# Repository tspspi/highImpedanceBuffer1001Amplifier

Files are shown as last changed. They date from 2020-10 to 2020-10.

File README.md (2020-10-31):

# Simple combined buffer and 1001x amplifier

This is a simple circuit that combines two OpAmps with 1 GHz
bandwidth to form a buffer amplifier followed by an 1001 times
amplifying amplifier.

This circuit has been designed to measure the beam profile of
an low current electron beam. The shunt has been designed as wire
resistor to be easily adaptable. The OpAmps have been selected
with up to 1 GHz bandwidth to allow for measurement of deflection
frequency inside an modulated beam.

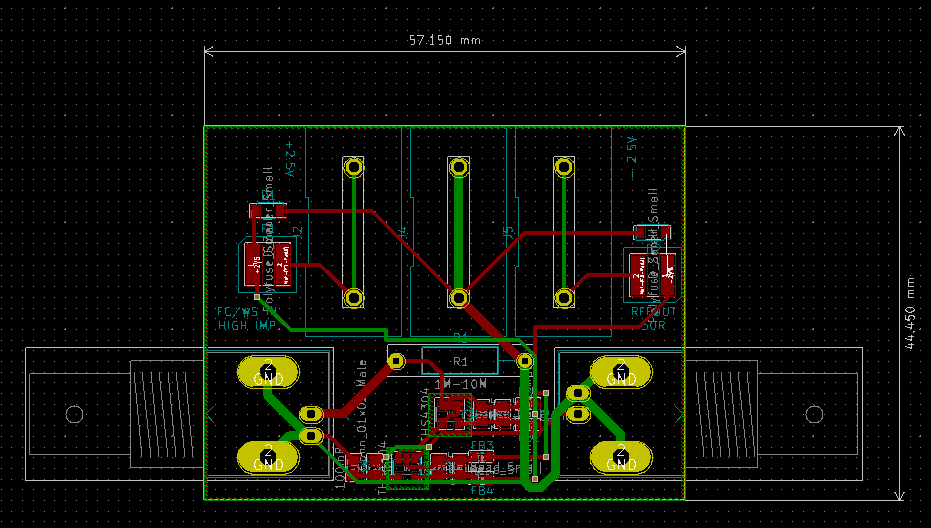
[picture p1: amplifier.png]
PCB layout


Schematic

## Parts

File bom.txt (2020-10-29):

#	FarnellNo	Title																								Unit price		Price
2	1076296		BNC Connector																				 2.920				 5.840
1	2519856		100 R +- 0.1%, 100 mW																 0.883				 0.883
1	2328114		100 mR																							 0.114				 1.114
2	3117744		THS4304																							 6.030				12.060
2	1759412		3.3 uF																							 0.165				 0.825
2	1740665		0.1 uF																							 0.0953				 0.953
4	3282195		Ferrite Beds																				 0.026			   0.104
1 	1698986		Banenstecker Buchse 4mm, grün												 1.89					 1.89
1 	1698983		Banenstecker Buchse 4mm, schwarz										 1.89					 1.89
1 	1698982		Banenstecker Buchse 4mm, rot												 1.89					 1.89
2	2285354		Zener-Diode, 3 V, 1 W, SOD-123F											 0.0832				0.1664
2 	1822219		Rückstellbare Sicherung, PPTC, 2016 (550 mA)				 0.9520				1.9040

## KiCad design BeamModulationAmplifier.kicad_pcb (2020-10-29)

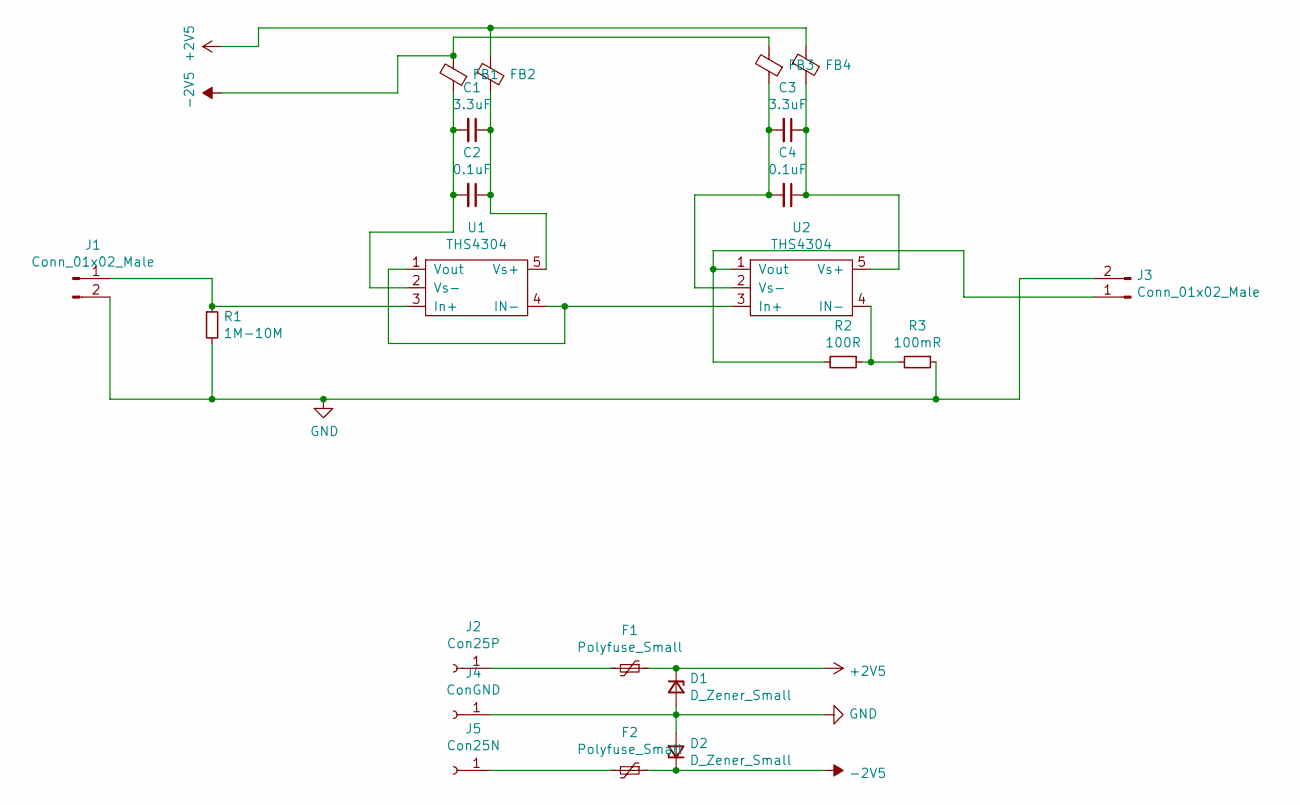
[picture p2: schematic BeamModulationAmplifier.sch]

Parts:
C1, C3: 3.3uF; R_0805_2012Metric
C2, C4: 0.1uF; R_0805_2012Metric
D1, D2: D_Zener_Small; Mini2
F1, F2: Polyfuse_Small; Generic2016
FB1, FB2, FB3, FB4: Ferrite_Bead_Small; R_0603_1608Metric; FarnellNo 3282195
J1, J3: Conn_01x02_Male; BNC_Amphenol_B6252HB-NPP3G-50_Horizontal; FarnellNo 1076296
J2: Con25P; 24.243
J4: ConGND; 24.243
J5: Con25N; 24.243
R1: 1M-10M; R_Axial_DIN0309_L9.0mm_D3.2mm_P15.24mm_Horizontal
R2: 100R; R_0805_2012Metric
R3: 100mR; R_0805_2012Metric
U1, U2: THS4304; SOT-23-5

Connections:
+2V5: D1.1 (K), F1.1, FB2.1, FB4.1
-2V5: D2.1 (K), F2.1, FB1.2, FB3.2
GND: D1.2 (A), D2.2 (A), J1.2, J3.2, J4.1, R1.2, R3.1
unnamed: C1.1, C2.1, FB2.2, U1.5 (Vs+)
unnamed: C1.2, C2.2, FB1.1, U1.2 (Vs-)
unnamed: C3.1, C4.1, FB4.2, U2.5 (Vs+)
unnamed: C3.2, C4.2, FB3.1, U2.2 (Vs-)
unnamed: F1.2, J2.1, J2.2
unnamed: F2.2, J5.1, J5.2
unnamed: J1.1, R1.1, U1.3 (In+)
unnamed: J3.1, R2.2, U2.1 (Vout)
unnamed: R2.1, R3.2, U2.4 (IN-)
unnamed: U1.1 (Vout), U1.4 (IN-), U2.3 (In+)

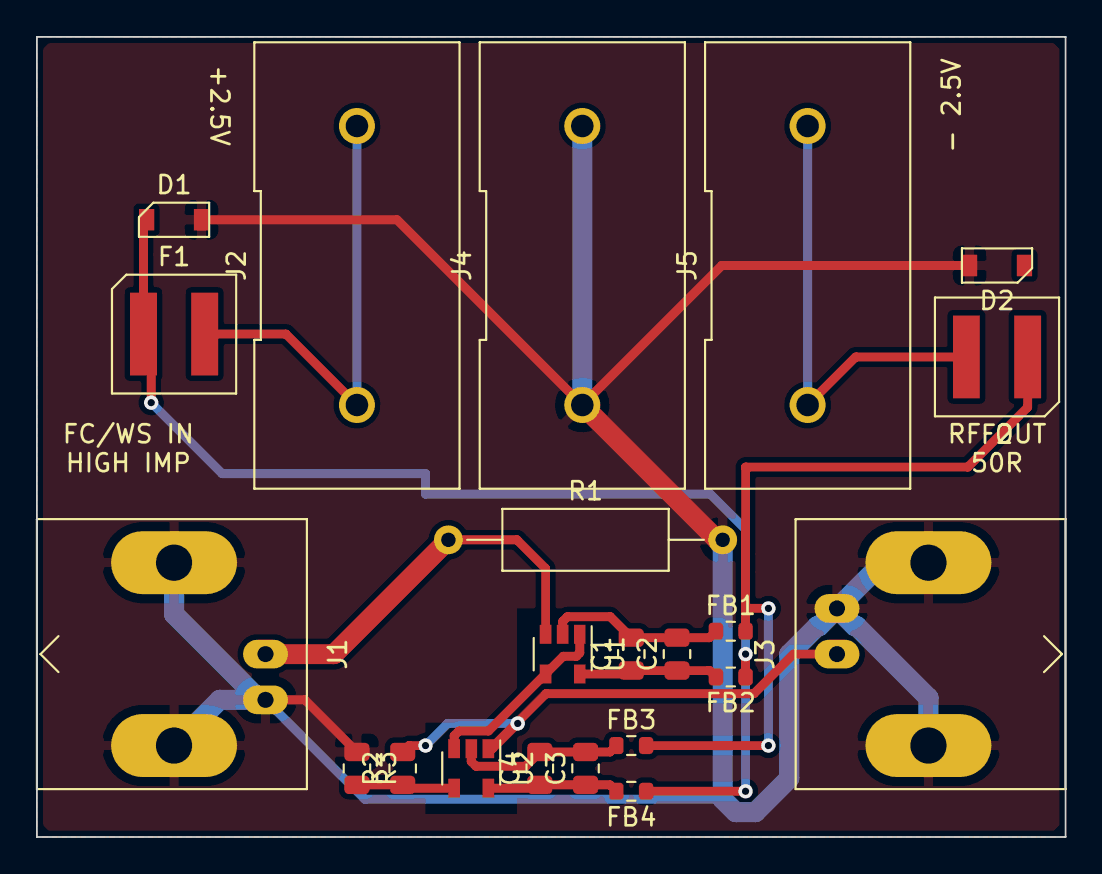
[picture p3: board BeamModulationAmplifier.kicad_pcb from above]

Board: 2 copper layers, 57.2 x 44.5 mm, 22 parts (0 on the bottom side), 13 nets.
